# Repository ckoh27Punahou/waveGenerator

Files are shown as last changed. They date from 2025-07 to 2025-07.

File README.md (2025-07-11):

# Wave Generator Documentation

## Wave Generator Purpose

This project was developed to help support outreach efforts in Hawaii's educational sector, specifically in regards to further educating the use about waves and wave energy. 

This github page aims to provide adequate documentation for a desktop wave generator. It should provide **CAD Files, COTS BOM, Electrical Diagrams, and Source Code**. 

# CAD Files

## File Formatting

This wave generator is constructed using 3D printed and supplementary COTS parts (Commercial Off The Shelf). **The CAD files are posted as .STEP files**, meaning that they are ***NOT*** meshes (fully editable geometry). 

## Print Settings

The 3D printed parts (for working models) should be printed out of PLA or PETG. Settings are as follow: 3-5 walls, 25-45% infill. Prints should be within +-0.2mm of tolerance. Adjust to printer as necessary. 

## CAD BOM

The [Bill of Materials](https://github.com/ckoh27Punahou/waveGenerator/blob/main/Docs/waveGeneratorBOM.csv) to all of the COTS parts is posted as a .csv within the Docs folder. 

# Source Code

This wave generator uses code to take user input via rotary encoders and calculate the proper settings to generate the user specified waves. There are two options for source code: using Visual Studio's Platform IO, or using the official Arduino IDE. There are two versions of the code posted above (identical) - each is designed for the specific program. 

## Development Platforms

This code was developed specifically for the [Arduino Nano ESP32](https://store.arduino.cc/products/nano-esp32-with-headers?srsltid=AfmBOoobrec-nGruFs_-Y9yvGQ6Ko73yMo6Cp1iv4HudvSx1w5w5968Y) using the Arduino configuration. The development platform was Visual Studio Code, which utilized Platform IO to push the code to the Arduino and include the necessary libraries. Versions for the Arduino IDE and VS Code are both posted above (**Install Accordingly**). 

## Installing Libraries

The following library dependencies need to be installed (either using Platform IO or the Arduino IDE): AccelStepper.h, hd44780.h, hd44780_I2Cexp.h - this is done externally of the written software. 

[How to install libraries in Platform IO](https://community.platformio.org/t/adding-libraries-to-project/25807)

[How to install libaries in Arduino IDE](https://docs.arduino.cc/software/ide-v1/tutorials/installing-libraries/)

# Electrical Wiring

[Electrical wiring diagram](https://github.com/ckoh27Punahou/waveGenerator/blob/main/Docs/waveGeneratorElectricalDiagram.pdf) is posted in the Docs folder ("waveGeneratorElectricalDiagram.pdf"). 

# Assembly

Assembly for this project is relatively simple. It goes as follows: electrical assembly and wiring, installing heat-set inserts, physical assembly, belt tensioning, and finally mounting. 

[Full assembly instructions](https://github.com/ckoh27Punahou/waveGenerator/blob/main/Docs/AssemblyInstructions.md) is posted in the Docs folder ("AssemblyInstructions.md")

# Usage

Usage for this project is relatively straightforward. After code has been uploaded and mechanical and electrical systems have been constructed, the following instructions can be used: 

[Usage Instructions](https://github.com/ckoh27Punahou/waveGenerator/blob/main/Docs/UsageInstruction.md)

# Developer Notes

I'm Charlie Koh. At the time of this development, I am a rising Junior at Punahou High School. This project was developed in collaboration with the lab of Dr. Troy Heitmann.

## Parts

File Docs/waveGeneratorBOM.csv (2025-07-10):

Item # | Description | Link | Unit Quantity | Unit Price | Price
1 | Nema 17 | https://www.amazon.com/STEPPERONLINE-Stepper-Bipolar-Connector-compatible/dp/B00PNEQKC0 | 1 | $19.99 | $19.99 | Total Price
2 | DM556Y Stepper Driver | https://www.amazon.com/STEPPERONLINE-Digital-Stepper-1-7-5-6A-20-50VDC/dp/B082CWMTV2 | 1 | $25.19 | $25.19 | $134.51
3 | 20x4 LCD Display | https://www.amazon.com/Hosyond-Module-Display-Arduino-Raspberry/dp/B0C1G9GBRZ | 1 | $5.67 | $5.67
4 | Rotary Encoder | https://www.amazon.com/WGCD-KY-040-Degree-Encoder-Arduino/dp/B07B68H6R8 | 2 | $1.56 | $3.12
5 | 24v to 5v Buck Converter | https://www.digikey.com/en/products/detail/pololu/2858/10451183 | 1 | $18.95 | $18.95
6 | 300mmx8mm Carbon Fiber Rod | https://www.amazon.com/FANCYWING-400MMX-1-0MM-Carbon-Airplane/dp/B0BJ1HZYZQ?sp_csd=d2lkZ2V0TmFtZT1zcF9hdGY | 4 | $4.40 | $17.60
7 | Timing Belt System | https://www.amazon.com/KeeYees-Timing-Tensioner-Torsion-Printer/dp/B07JKT5BZQ/ref=sr_1_15?sr=8-15 | 1 | $14.99 | $14.99
8 | 15mmx15mmx8mm Linear Bearing | https://www.amazon.com/RJ4JP-01-08-Bearing-Printer-Replacement-Diameter/dp/B099665RSK | 4 | $1.46 | $5.84
9 | 17mmx6mmx6mm Ceramic Bearing | https://www.amazon.com/gp/product/B0B5XN4FFV/ref=ewc_pr_img_1?smid=A1THAZDOWP300U&th=1 | 1 | $1.64 | $1.64
10 | M4 Heat Set Insert | https://www.amazon.com/HANGLIFE-Heat-Set-Threaded-Printing-Components/dp/B0CS6XGMFD | 30 | $0.10 | $3.00
11 | 20mm M4 Bolt | https://www.amazon.com/BNUOK-180pcs-Stainless-Threads-Spanner/dp/B0DYNJPYV7?sp_csd=d2lkZ2V0TmFtZT1zcF9tdGY | 22 | $0.07 | $1.54
12 | 12mm M4 Bolt | https://www.amazon.com/Fullerkreg-Socket-Stainless-Machine-Quantity/dp/B07CJ7PTRS?sp_csd=d2lkZ2V0TmFtZT1zcF9hdGY | 16 | $0.11 | $1.76
13 | 25mm Steel Dowel | https://www.amazon.com/ZDingTech-Support-Shelves-Rod-304-Stainless/dp/B0F28QSRGD | 1 | $0.23 | $0.23
14 | 1 kg PETG | https://www.amazon.com/Polymaker-PB01001-PolyLite-hitzebest%C3%A4ndig-Zugfestigkeit/dp/B09DKRTSXW?s=industrial&sp_csd=d2lkZ2V0TmFtZT1zcF9hdGY | 1 | $15 | $15

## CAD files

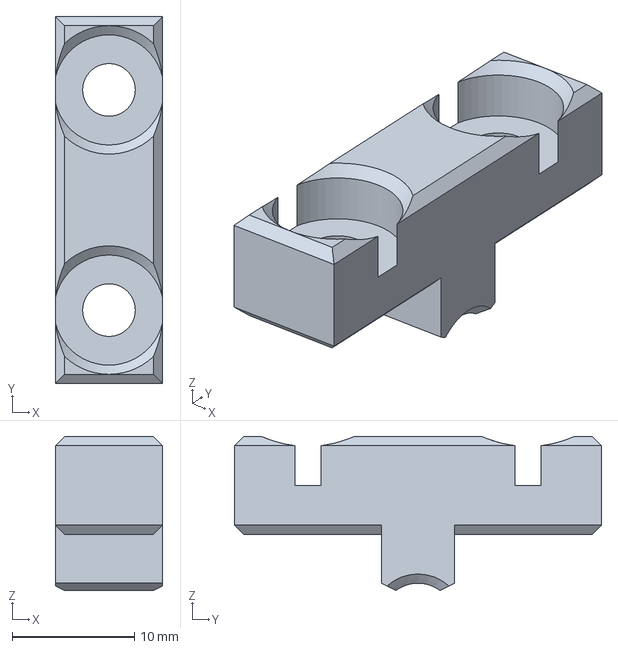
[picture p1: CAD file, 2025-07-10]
CAD_Files/Wave Generator CAD/Wave Generator - Pulley Seal 2.step
8.75 x 30.0 x 12.6 mm

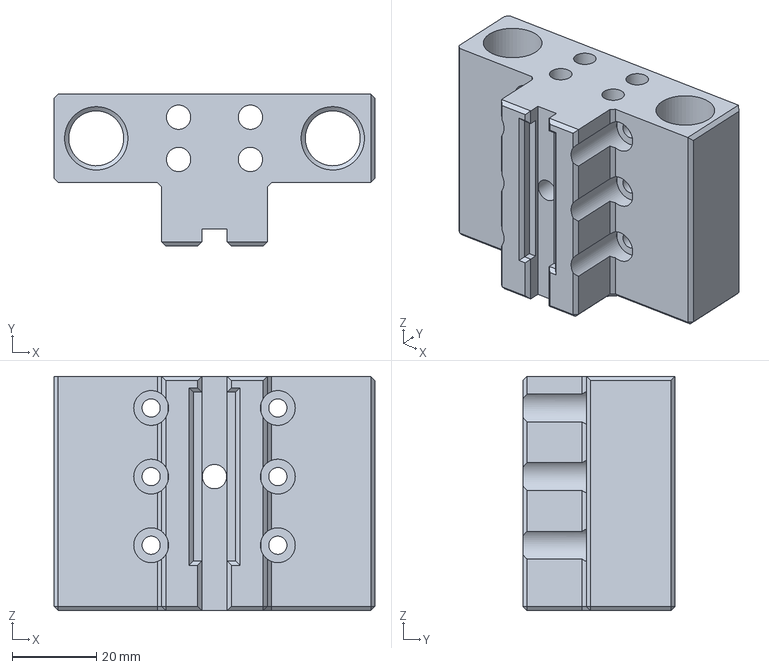
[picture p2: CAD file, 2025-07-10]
CAD_Files/Wave Generator CAD/Wave Generator - Wave Carrier.step
76.0 x 36.0 x 55.5 mm

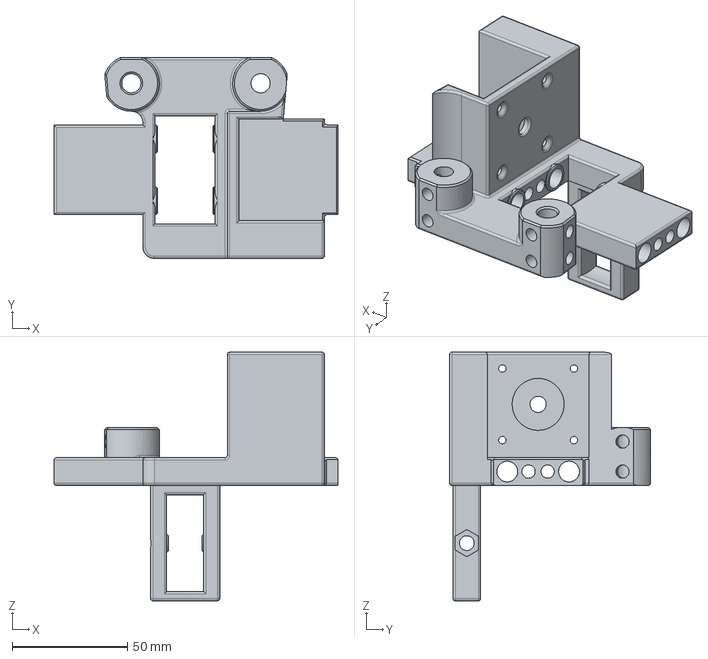
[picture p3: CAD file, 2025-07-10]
CAD_Files/Wave Generator CAD/Wave Generator - Motor Mount.step
123.0 x 87.0 x 107.7 mm

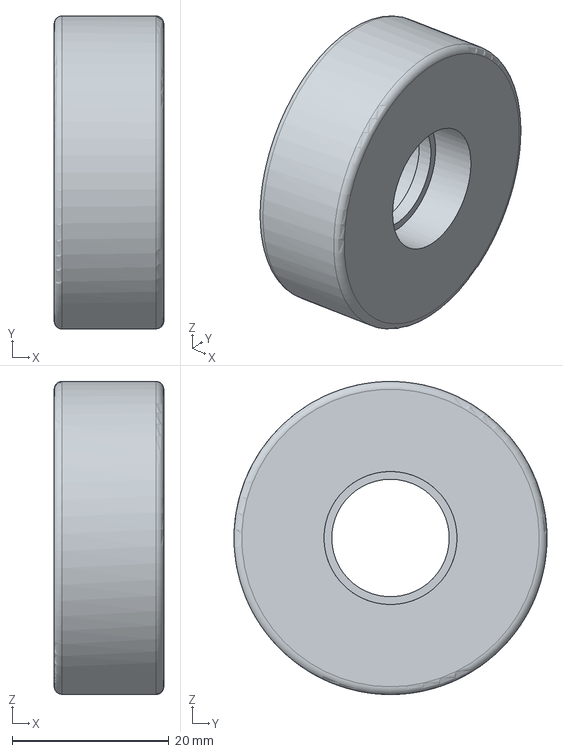
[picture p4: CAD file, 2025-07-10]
CAD_Files/Wave Generator CAD/Wave Generator - Idler Pulley.step
14.0 x 40.0 x 40.0 mm

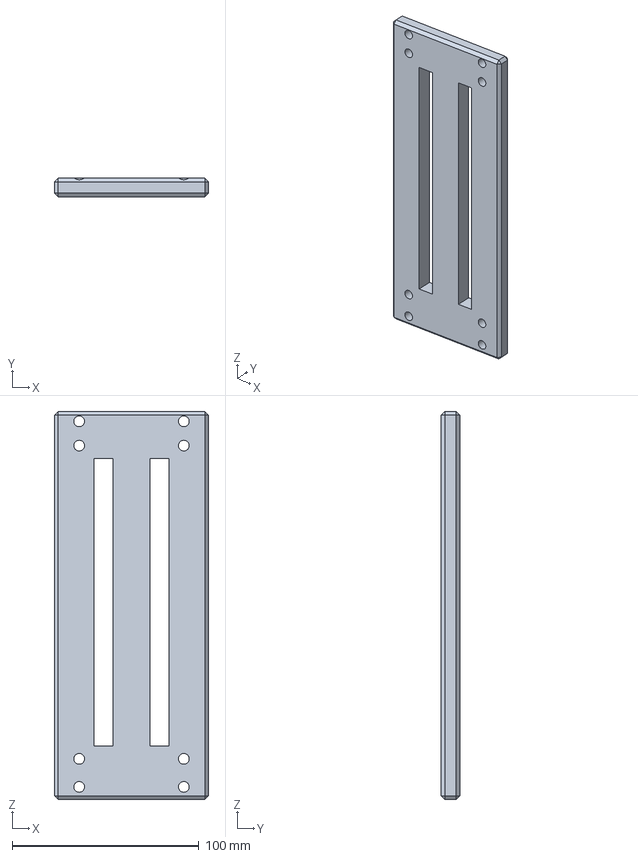
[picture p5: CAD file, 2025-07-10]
CAD_Files/Wave Generator CAD/Wave Generator - Wedge Backfill Cover.step
82.5 x 10.00 x 207.7 mm

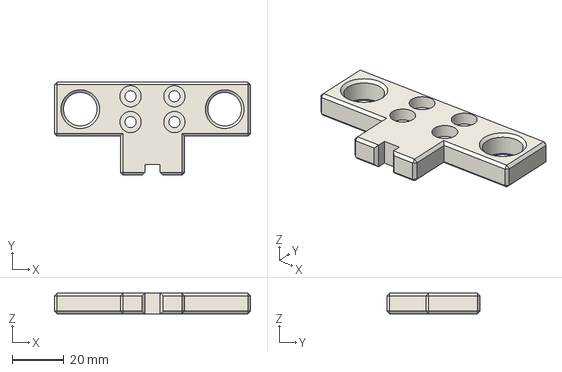
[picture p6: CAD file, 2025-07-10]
CAD_Files/Wave Generator CAD/Wave Generator - Wave Carrier Seal.step
76.0 x 36.0 x 8.00 mm

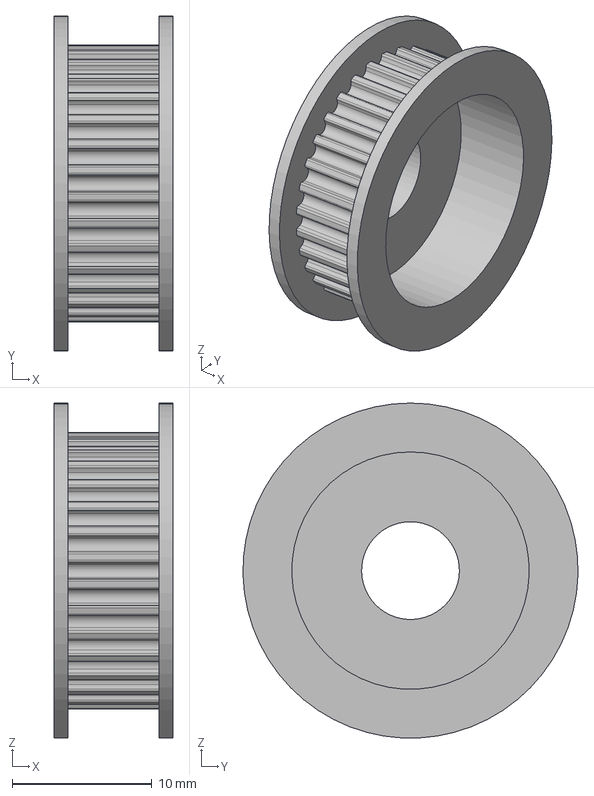
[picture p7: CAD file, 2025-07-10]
CAD_Files/Wave Generator CAD/Wave Generator - Lower Pulley.step
8.50 x 24.0 x 24.0 mm

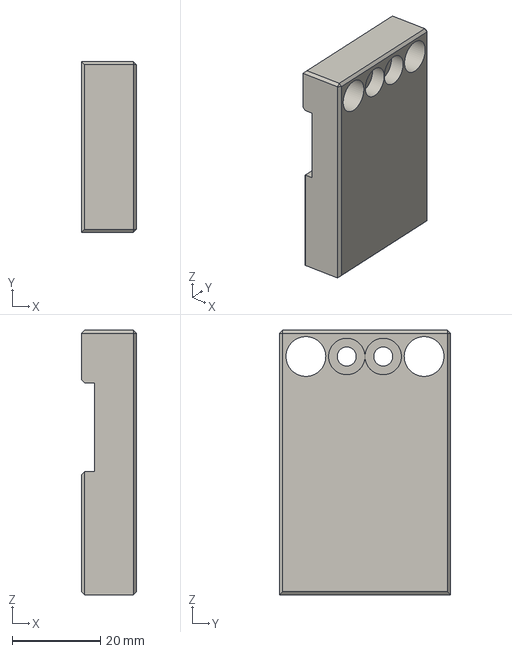
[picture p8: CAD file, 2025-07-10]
CAD_Files/Wave Generator CAD/Wave Generator - Outer Grab.step
12.5 x 38.8 x 60.0 mm

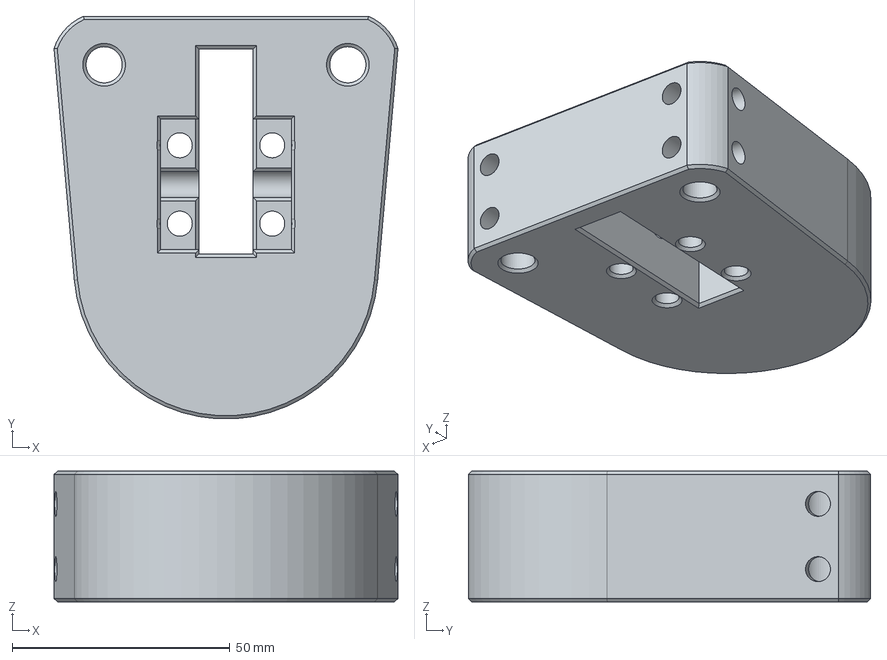
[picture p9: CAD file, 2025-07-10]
CAD_Files/Wave Generator CAD/Wave Generator - Lower Mount.step
79.0 x 92.5 x 30.0 mm

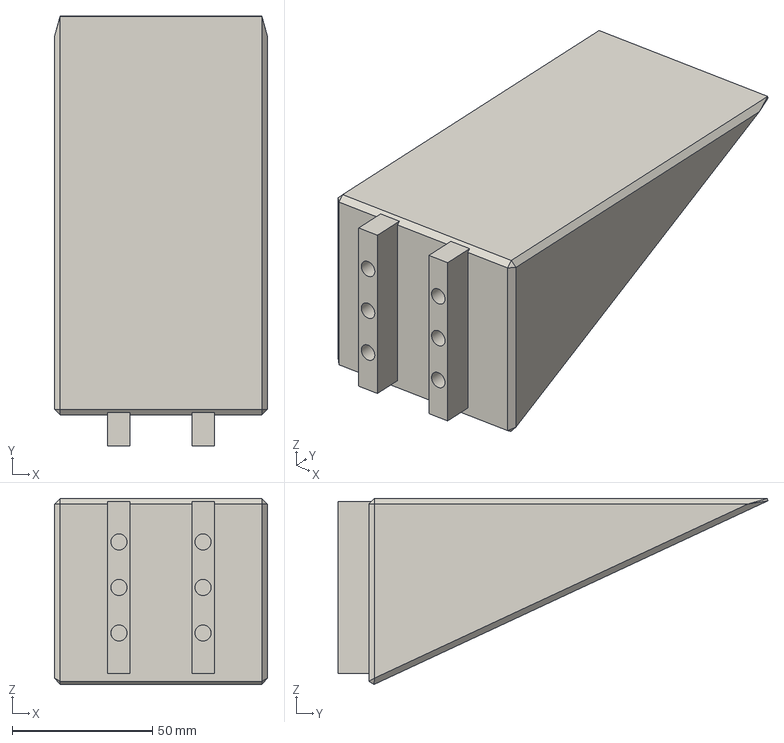
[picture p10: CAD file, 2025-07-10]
CAD_Files/Wave Generator CAD/Wave Generator - Wedge.step
76.0 x 153.4 x 66.4 mm

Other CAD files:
CAD_Files/Wave Generator CAD/Wave Generator - Pulley Seal.step
CAD_Files/Wave Generator CAD/Wave Generator - Outer Grab 2.step

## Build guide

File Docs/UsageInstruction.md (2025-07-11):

# Usage Procedure (Uploaded Arduino Code)

This is an instructional guide on how to use the wave generator after code has been uploaded. 

## Definitions (Repeated Later): 

**Wedge Angle:** The bottom angle of the wedge (between the hypotenuse and mounting side). Should be labeled at the top of the wedge. 
**Starting Depth:** The starting depth of the wedge. Measured as the deepest point of the wedge to the surface of the still water. Can be approximated (+-5mm). 
**Tank Depth:** The water depth in the tank. Measured from the bottom of the tank to the surface of the still water. 
**Amplitude:** The amplitude of the generated wave in millimeters. This is not completely accurate at the moment. During hardcaps (capping of amplitude at certain frequencies due to mechanical limits), the LCD will notify what the new hardcapped frequency is. The stroke length of the wedge corresponds with amplitude (via calculations involving all of the aforementioned variables and frequency), but does **not directly resemble the amplitude**. 
**Frequency:** The frequency of the generated wave in Hz. Frequency will always take priority over amplitude if mechanical limits are encountered (calculated by system internals - these are either speed caps or mechanical limits). 

## Step 0: Confirm Electrical Systems

Confirm that all electrical systems (particularly the buck converter) are wired exactly as the diagram shows. 

Move the wedge to the top of the movement range (as close as possible to the motor)

## Step 1: Plug Battery In

Plug the battery (24v 2.8aH) into the power adapter. The Arduino Nano ESP32 should have a small green LED light up. The motor driver (DM556Y) should also have a green LED light up. 

The LCD should light up, and should display some brief introduction text. 

## Step 2: Setting Initial Settings

### ***NOTE: You will not be able to change wedge angle, starting depth, or tank depth after the initialization phase. To reset, turn the system on and off***

After the LCD turns on, read the introductory text. After all text prompts disappear, it will ask to set a wedge angle. For this setting, either dial works to adjust the value (adjustments are +-1 degree). To confirm the value (after set to the desired value), push down on either of the dials (there is a button within the encoder).

It will then ask to set starting depth and tank depth. The top dial corresponds with starting depth, while the bottom dial corresponds with the tank depth. Set starting depth (the distance of the deepest wedge point from the surface of still water) and tank depth (the depth of water within the tank) to the nearest millimeter (adjustments are +-1 mm). To confirm starting depth, push down on the top dial. To confirm tank depth, push down on the bottom dial. 

After both starting and tank depth are confirmed, it will then ask for a **starting frequency and starting amplitude**. The top dial corresponds with amplitude, and the bottom dial corresponds with frequency. To confirm amplitude, press down on the top dial. To confirm frequency, press down on the bottom dial. 

***NOTE: Amplitude refers to the target amplitude of the WAVE, not the stroke. The stroke and rotation of the motor are calculated using all inputs.***

After a few brief seconds, it should start making waves. 

## Step 3 (Optional): Wave Amplitude and Frequency Adjustments

To adjust the wave amplitude and frequency without going through the entire setup, push down on either dial. It will pause wave generation as new settings are entered. The top dial again corresponds with amplitude, and the bottom dial is again with frequency. To confirm either, push down on the corresponding dial. 

A few seconds after both settings are confirmed, wave generation will resume, but with the adjusted settings.

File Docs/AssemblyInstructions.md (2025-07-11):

# Assembly Instructions

## Required Materials

1. Soldering Iron
2. Solder
3. BOM COTS Parts ($134.51)
4. 3mm Hex Key
5. Phillips Head Screwdriver
6. 2mm Hex Key
7. PLA
8. 20 AWG Wire
9. Dupont Jumper Cables
10. Wire Cutters
11. Wire Stripper
12. Heat Shrink/Electrical Tape

## Step 1: Electrical Wiring

Construct the electrical diagram as shown ("waveGeneratorElectricalDiagram"). The junctions indicate soldered areas/wire electrical connections. Wires that cross but do not contain a junction on their intersection do not have any electrical connection. For safety, place electrical tape/heat shrink over soldered joints. 

## Step 2: Heat Set Inserts

**NOTE: For this step, use a soldering iron tip either specifically designed for heat set inserts, or be comfortable having potential PLA contamintation on the tip of the soldering iron.**

Using M4 Heat Set Inserts (included in the COTS BOM), place heat set inserts in all of the following designated locations (images shown below). Arrows with label "1" indicate heat set inserts. 

Heat set inserts ***MUST*** be put in straight. If they are not, and screws insertion is attempted, the insert may do one of the following:

1. Surface detachment (pulled out)
2. Cross threading (destroys thread)
3. Unable to insert (either due to misalignment or angling)

### Upper Diagram:

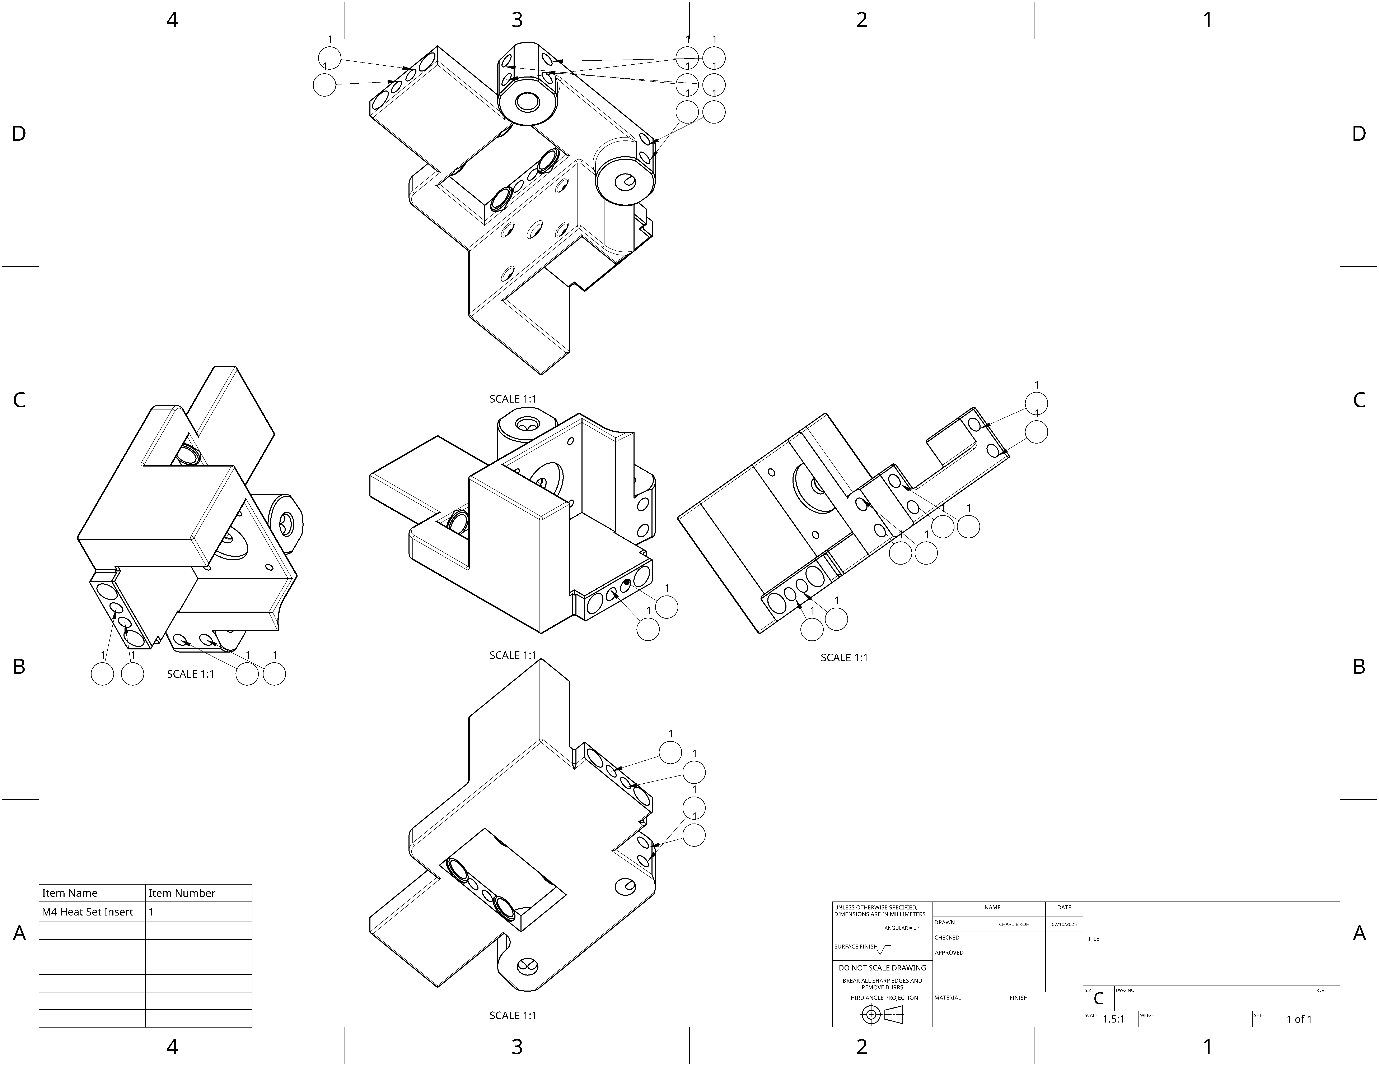
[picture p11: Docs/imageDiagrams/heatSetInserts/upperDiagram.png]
Upper Diagram


### Lower Diagram: 

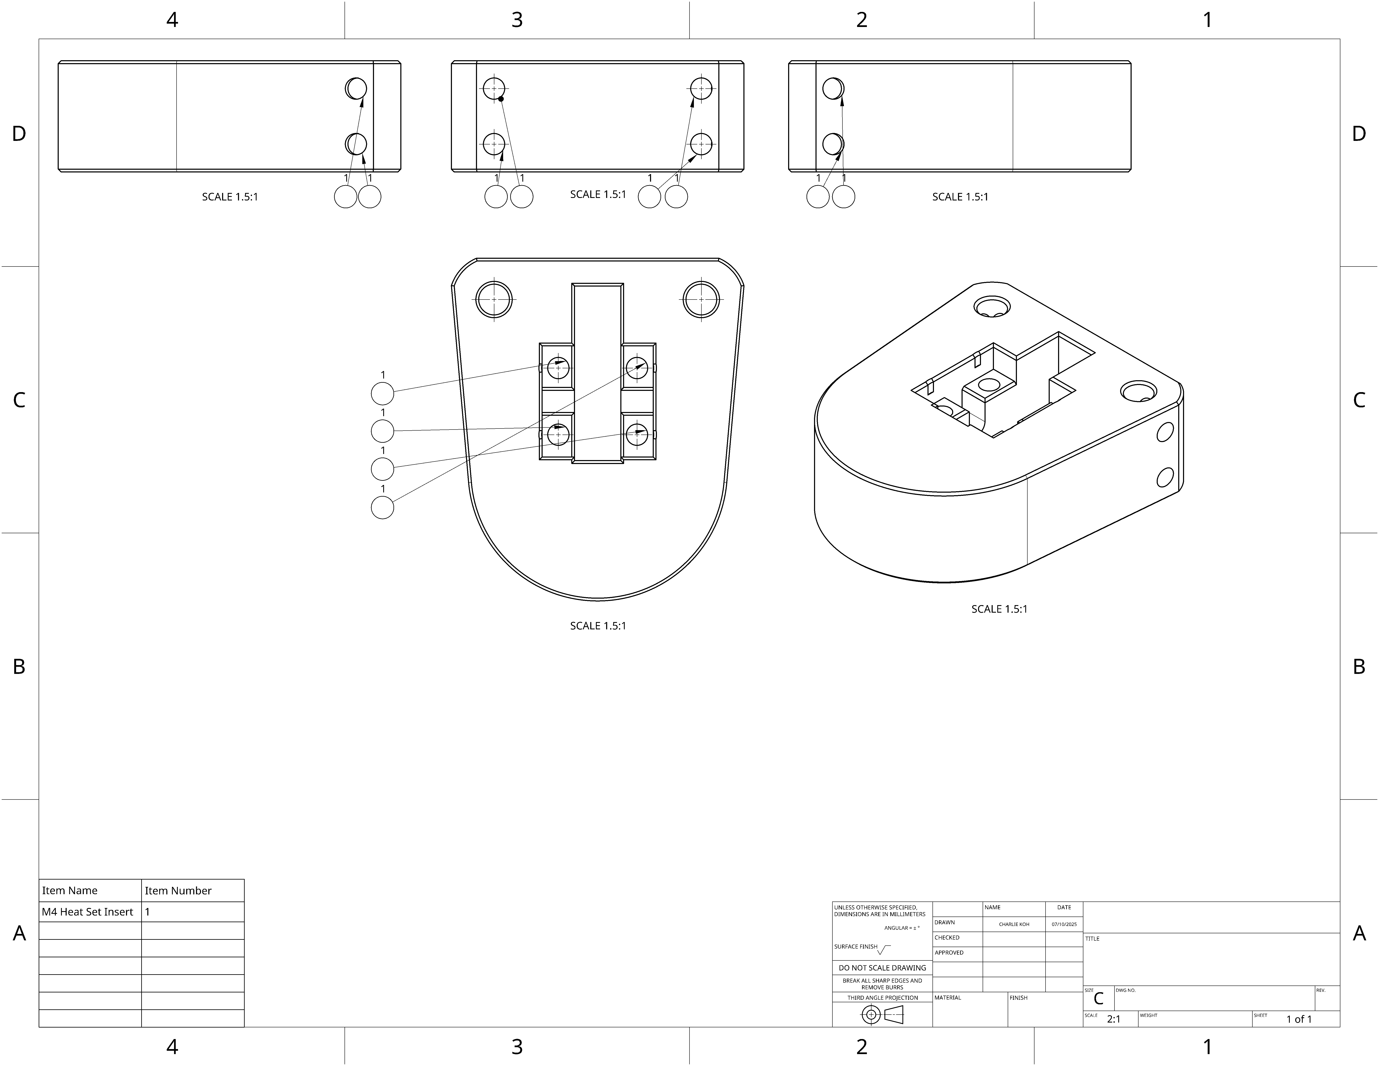
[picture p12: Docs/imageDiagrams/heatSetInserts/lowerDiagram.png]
Lower Diagram


### Wedge Diagram:

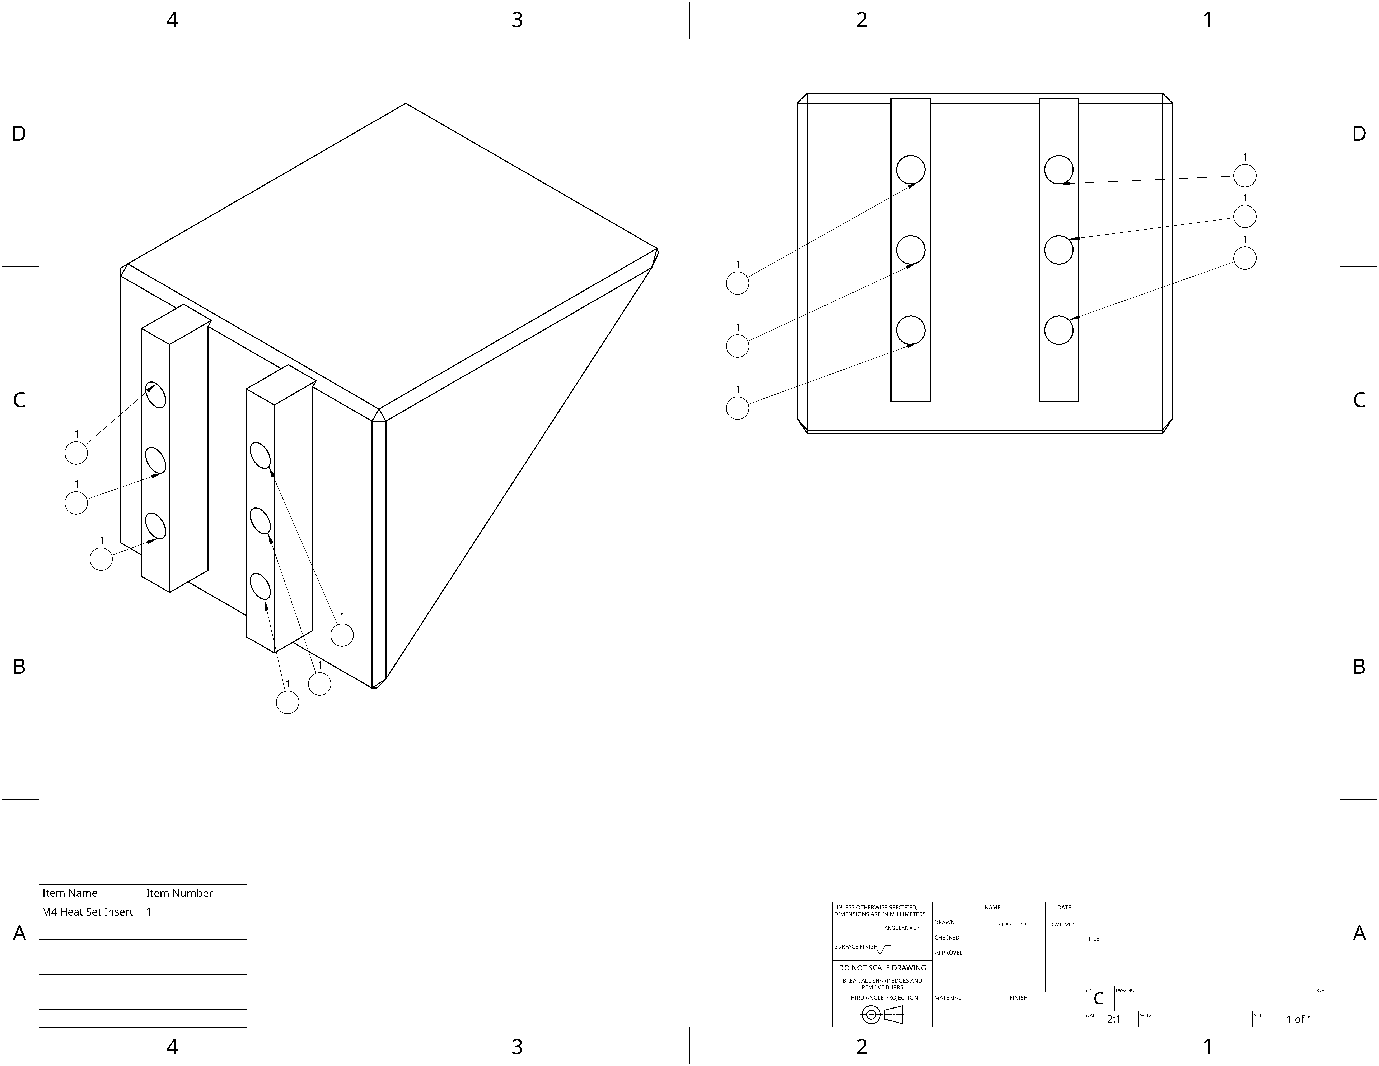
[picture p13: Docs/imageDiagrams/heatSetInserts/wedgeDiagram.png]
Wedge Diagram


## Step 3: Physical Assembly

### **Fully Exploded View**

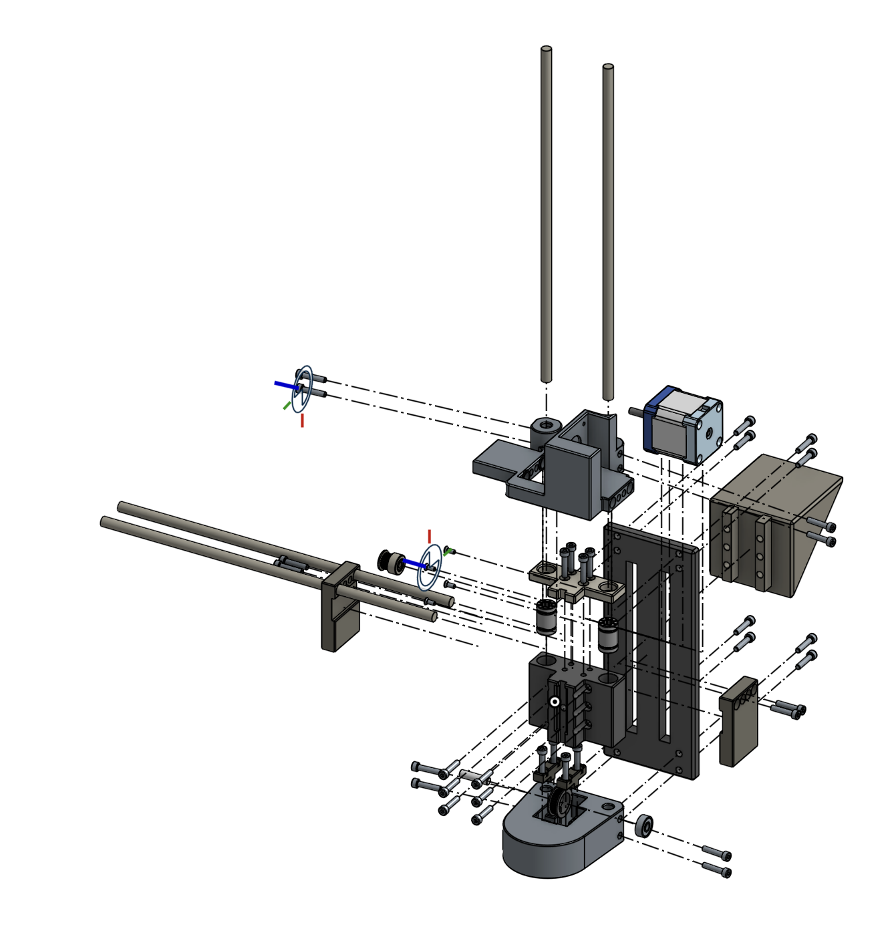
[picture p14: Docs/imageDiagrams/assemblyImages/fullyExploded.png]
Exploded View


### Step 3a: Insert Motor

Insert the motor as shown in the image below. Screw the motor in using the countersunk M3 screws (phillips head). 

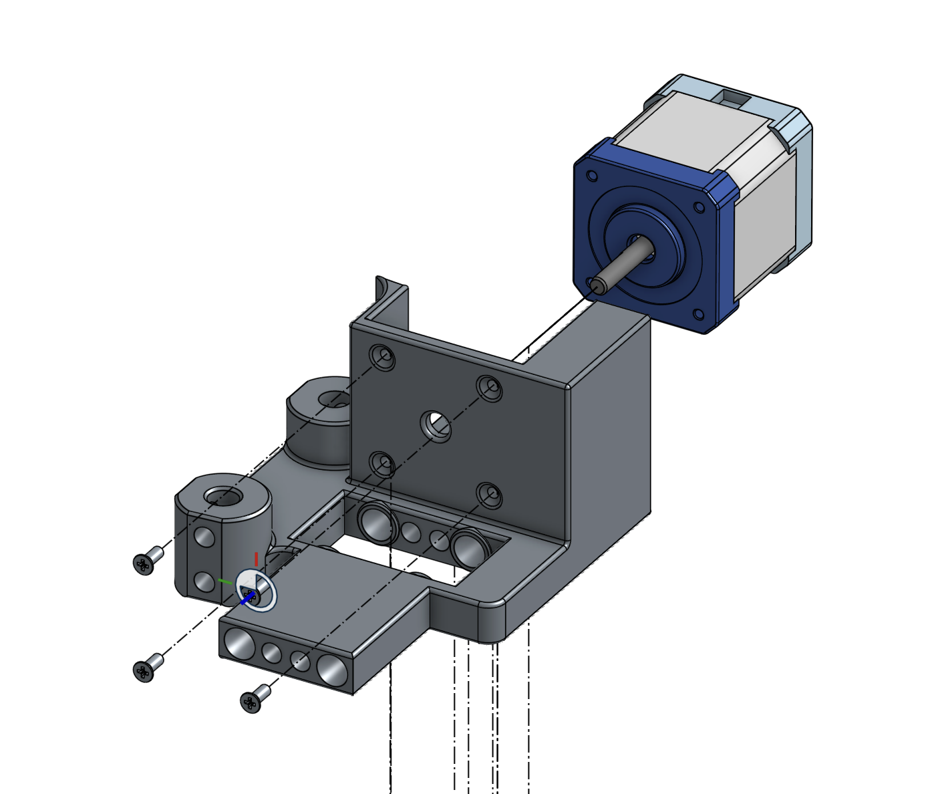
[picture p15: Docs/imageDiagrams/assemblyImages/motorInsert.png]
Motor Insert


### Step 3b: Insert Carbon Fiber Rod

Insert carbon fiber rod in the designated location of the motor mount. This won't be secured, and is used for structural support.

When inserting, make sure to simultaniously insert two linear bearings as shown below. These will be used to tension the belt.

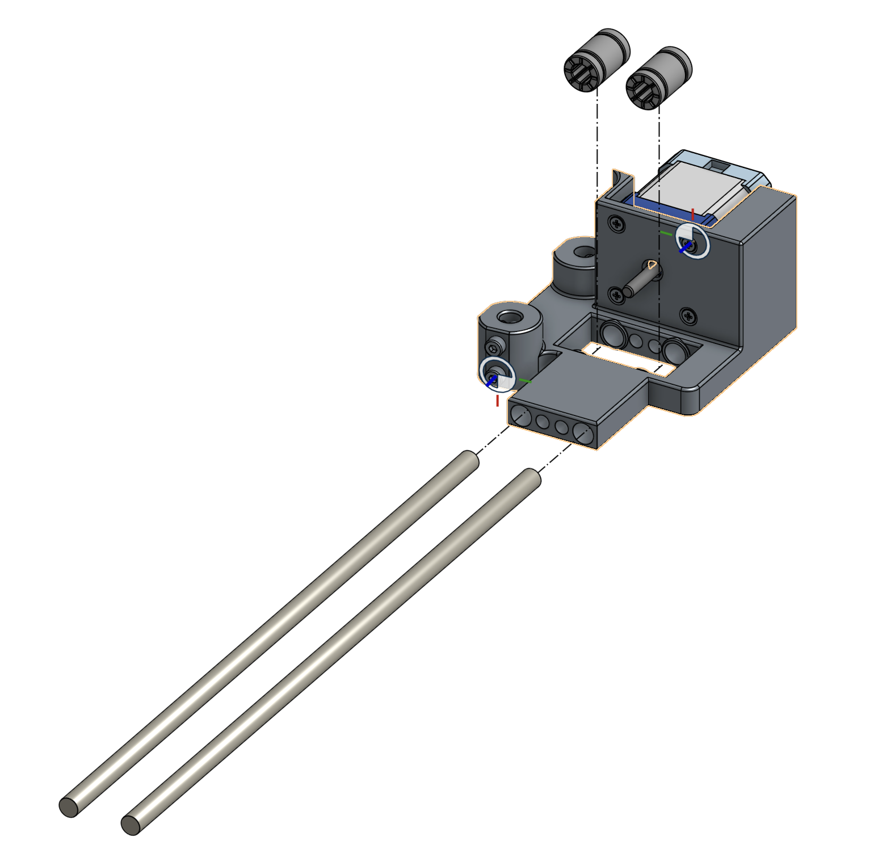
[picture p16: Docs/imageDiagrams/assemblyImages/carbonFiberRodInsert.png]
Carbon Fiber Rod Insert


### Step 3c: Assemble Carrier

Press fit linear bearings into the central carrige, and then screw the top cover onto the central carrige (as displayed below) using M4x20mm screws. 

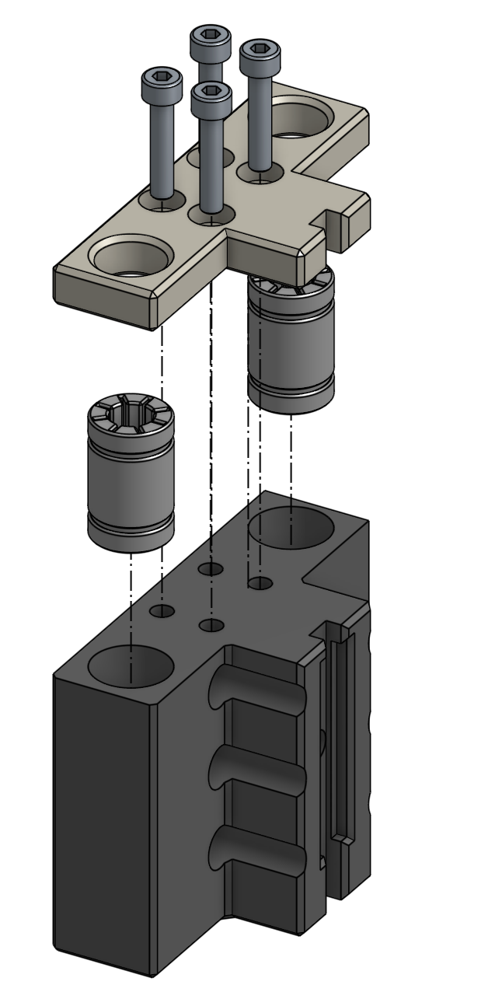
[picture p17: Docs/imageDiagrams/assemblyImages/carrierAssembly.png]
Carrier Assembly Diagram


### Step 3d: Assemble Lower Mount

Press fit 17mmx6mmx6mm bearing into lower pulley. Place pulley (with bearing) and pulley spacer onto 25mmx6mm steel dowel, and then insert into location on lower mount (displayed in image below).

Place lower seals to cover and secure 25mmx6mm steel dowel, and then secure with M4x20mm screws. 

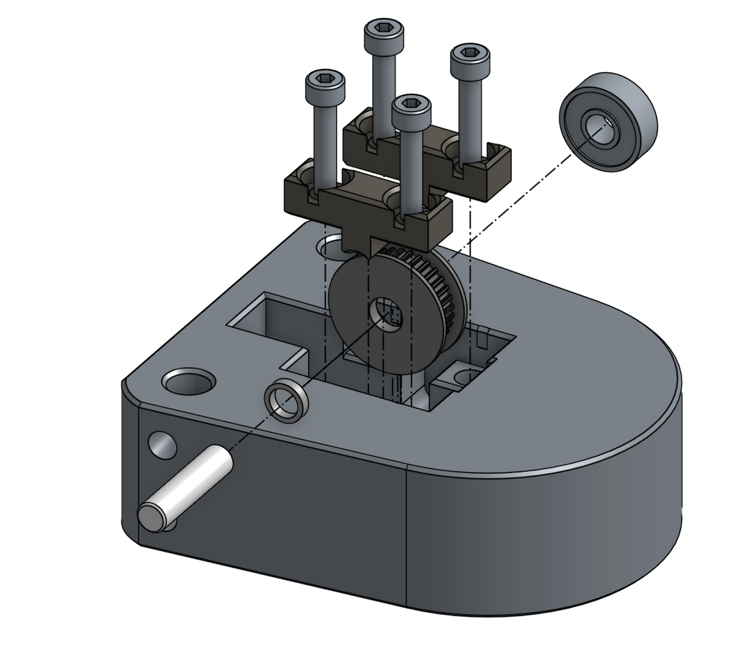
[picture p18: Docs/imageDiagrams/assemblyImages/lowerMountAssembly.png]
Lower Mount Assembly Diagram


### Step 3e: Insert Vertical Carbon Fiber Rods

Insert two 300mmx8mm Carbon Fiber Rods into the lower mount. Proceed to use M4x16mm screws to secure the carbon fiber rods (displayed in the image below - similar to set screws).

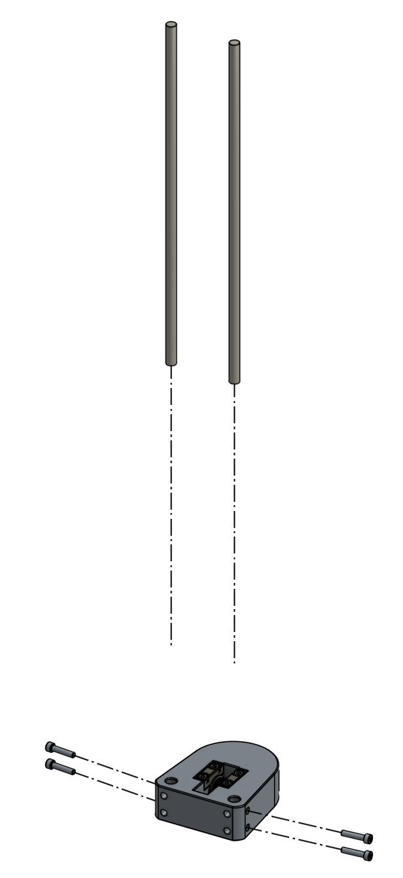
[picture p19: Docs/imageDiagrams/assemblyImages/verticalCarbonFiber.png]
Carbon Fiber Rod Insert


### Step 3f: Attach Motor Mount to Carbon Fiber Rods

Place the motor mount on the top of the two previously mounted vertical carbon fiber rods. Attach the front plate, and secure to the lower and motor mounts using M4x16mm screws. Similarly to the previous step, secure the carbon fiber rods with side M4x16mm screws (again, similar to set screws). 

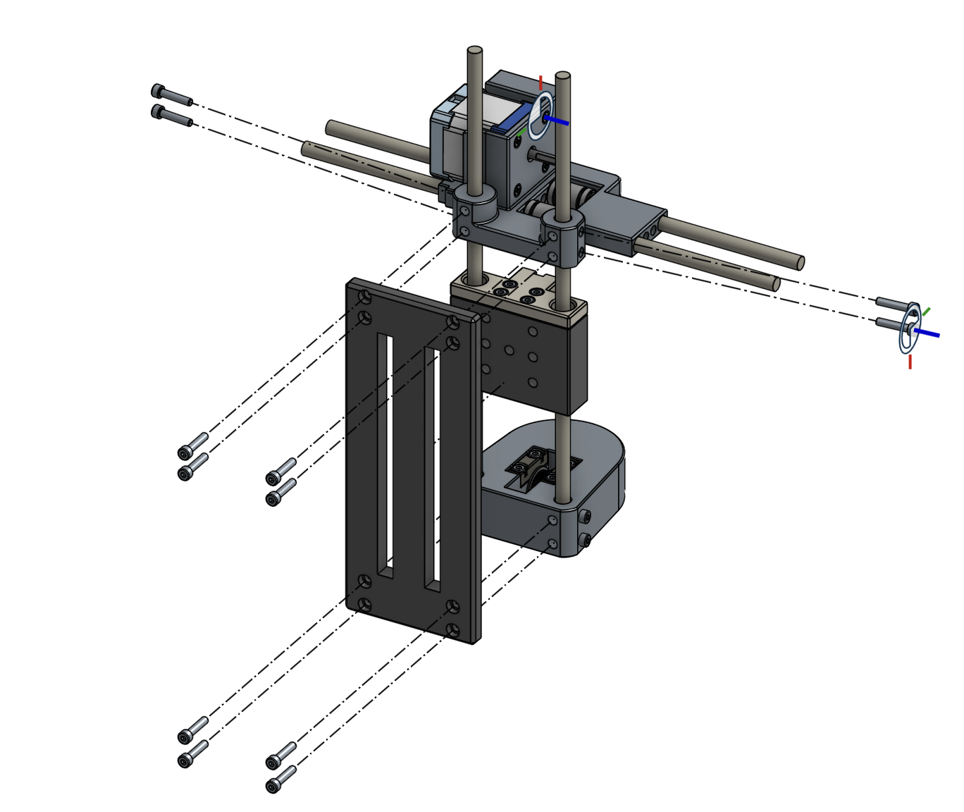
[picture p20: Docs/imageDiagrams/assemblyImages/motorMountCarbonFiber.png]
Motor Mount Carbon Fiber Insert


### Step 3g: Wedge Attachment

Place the front wedge stilts aligned with the central carrier. Use six M4x20mm screws to secure the wedge to the central carrier. 

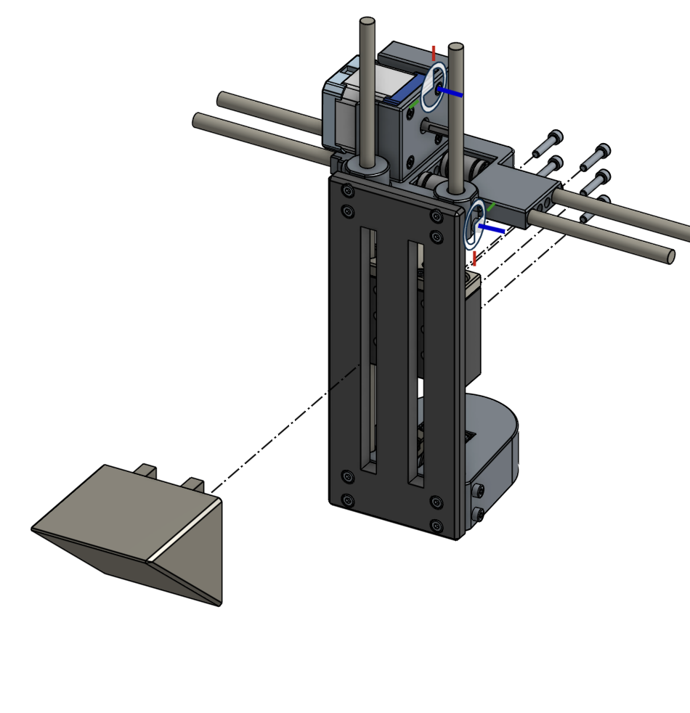
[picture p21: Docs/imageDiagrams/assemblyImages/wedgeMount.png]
Wedge Attachment Image


### Step 3h: Tank Mount 1

Place one of the outer mounts on the motor side of the motor mount, and secure it with two M4x20mm bolts. 

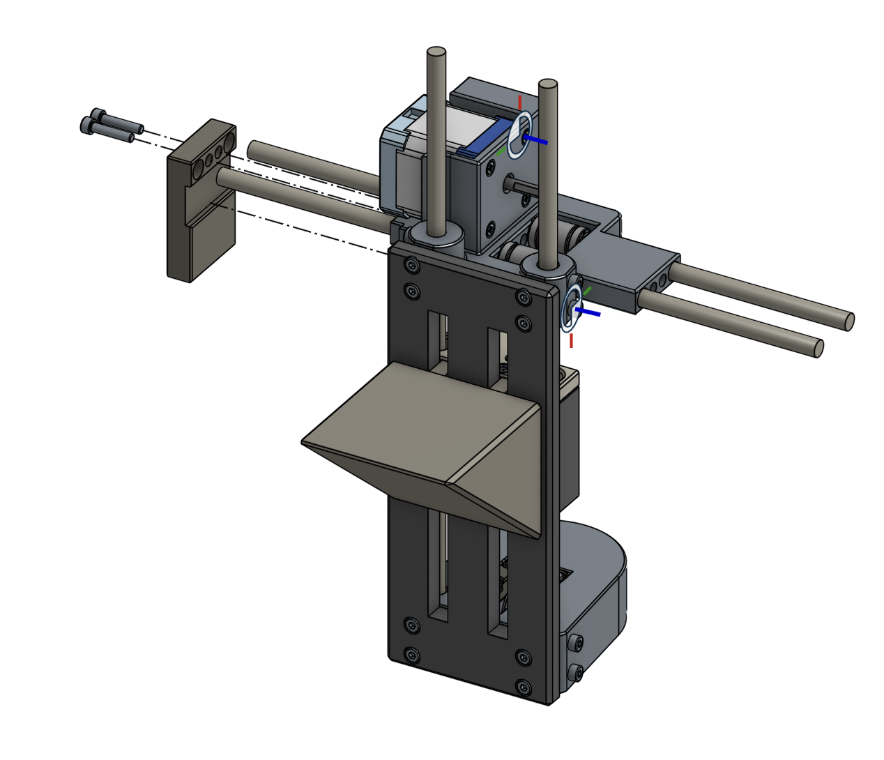
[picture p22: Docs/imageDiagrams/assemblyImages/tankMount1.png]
Tank Mount 1


### Step 3i: Mounting GT2 Pulley

Place 20T GT2 pulley onto the stepper motor shaft. 

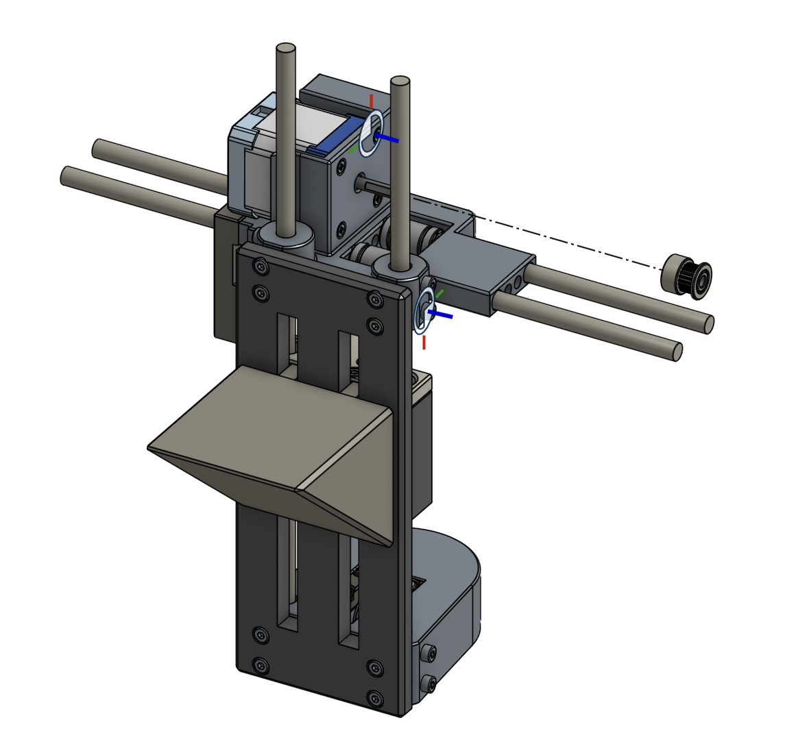
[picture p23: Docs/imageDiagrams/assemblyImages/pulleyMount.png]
Pulley Mounting


### Step 3j: Belt Mounting

Place belt around lower pulley and belt pulley, and place ends in the top and the bottom of the central carrier (not displayed). Place belt securer and M4x20mm bolt, and secure belt (with serrated side facing the belt and matching teeth) - make sure the belt is properly tensioned. 

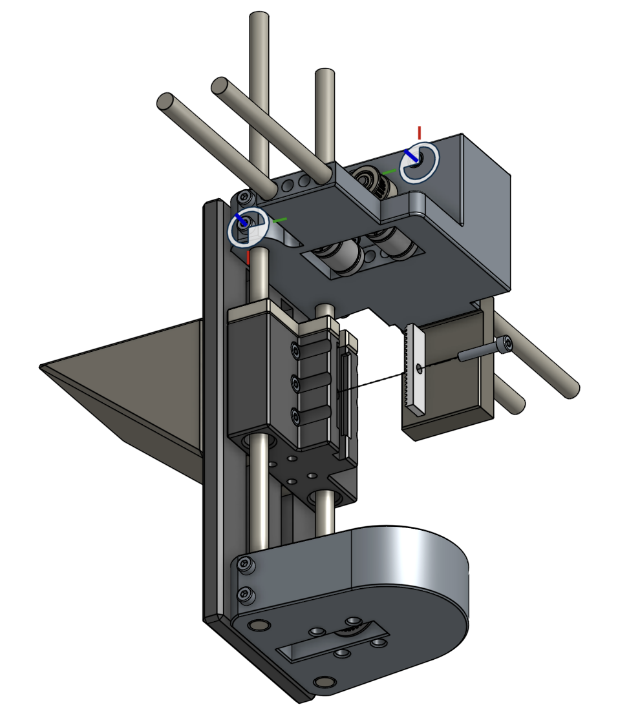
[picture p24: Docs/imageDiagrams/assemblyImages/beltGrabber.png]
Belt Mounting


### Step 3k: Tank Mounting

Place full assembly into the tank. Place second outer mount on the non-motor side of the motor mount, and secure around the tank using two M4x20mm screws.

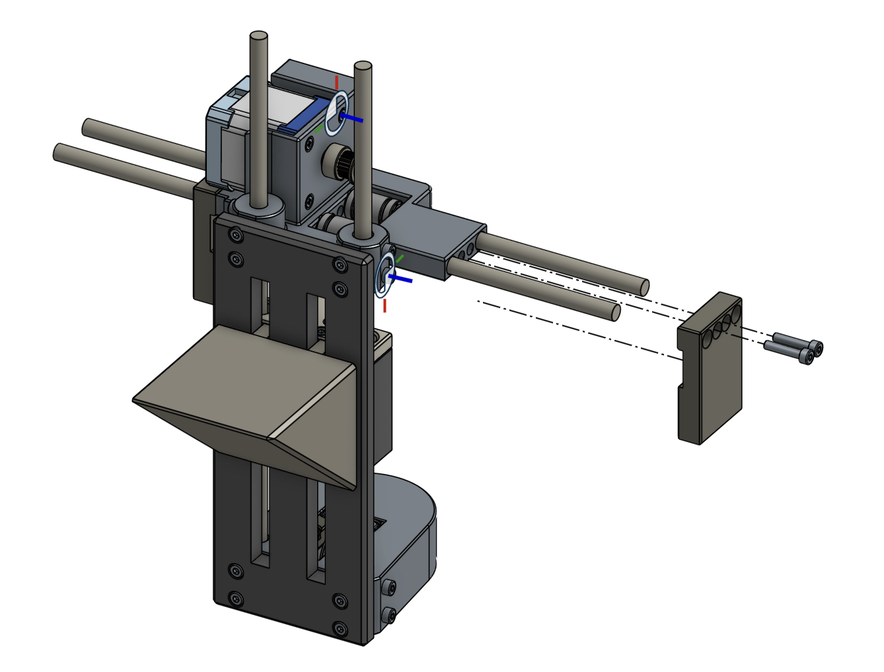
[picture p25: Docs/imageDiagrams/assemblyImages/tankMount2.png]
Tank Mounting


***Assembly of wave generator is completed***

## Step 4: Uploading Code

Prior to uploading code, choose to use either Visual Studio Code's Platform IO or the official Arduino IDE (easier). Download the corresponding file from this repository. 

Plug a data-capable USB-C cable into the Arduino Nano ESP32. Using either Platform IO or the Arduino IDE, make sure to import the following libraries (***NOT #include***): 

1. AccelStepper
2. hd44780
3. (For PIO, identify path) hd44780

[How to install libraries in Platform IO](https://community.platformio.org/t/adding-libraries-to-project/25807)

[How to install libaries in Arduino IDE](https://docs.arduino.cc/software/ide-v1/tutorials/installing-libraries/)

Using the computer port that the USB-C cable, upload the designed sketches (***Use the program either designed for Platform IO or Arduino IDE***). Once it states that uploding is complete, unplug the USB-C cable. 

***Transition to [User Manual](https://github.com/ckoh27Punahou/waveGenerator/blob/main/Docs/UsageInstruction.md) for usage instructions***

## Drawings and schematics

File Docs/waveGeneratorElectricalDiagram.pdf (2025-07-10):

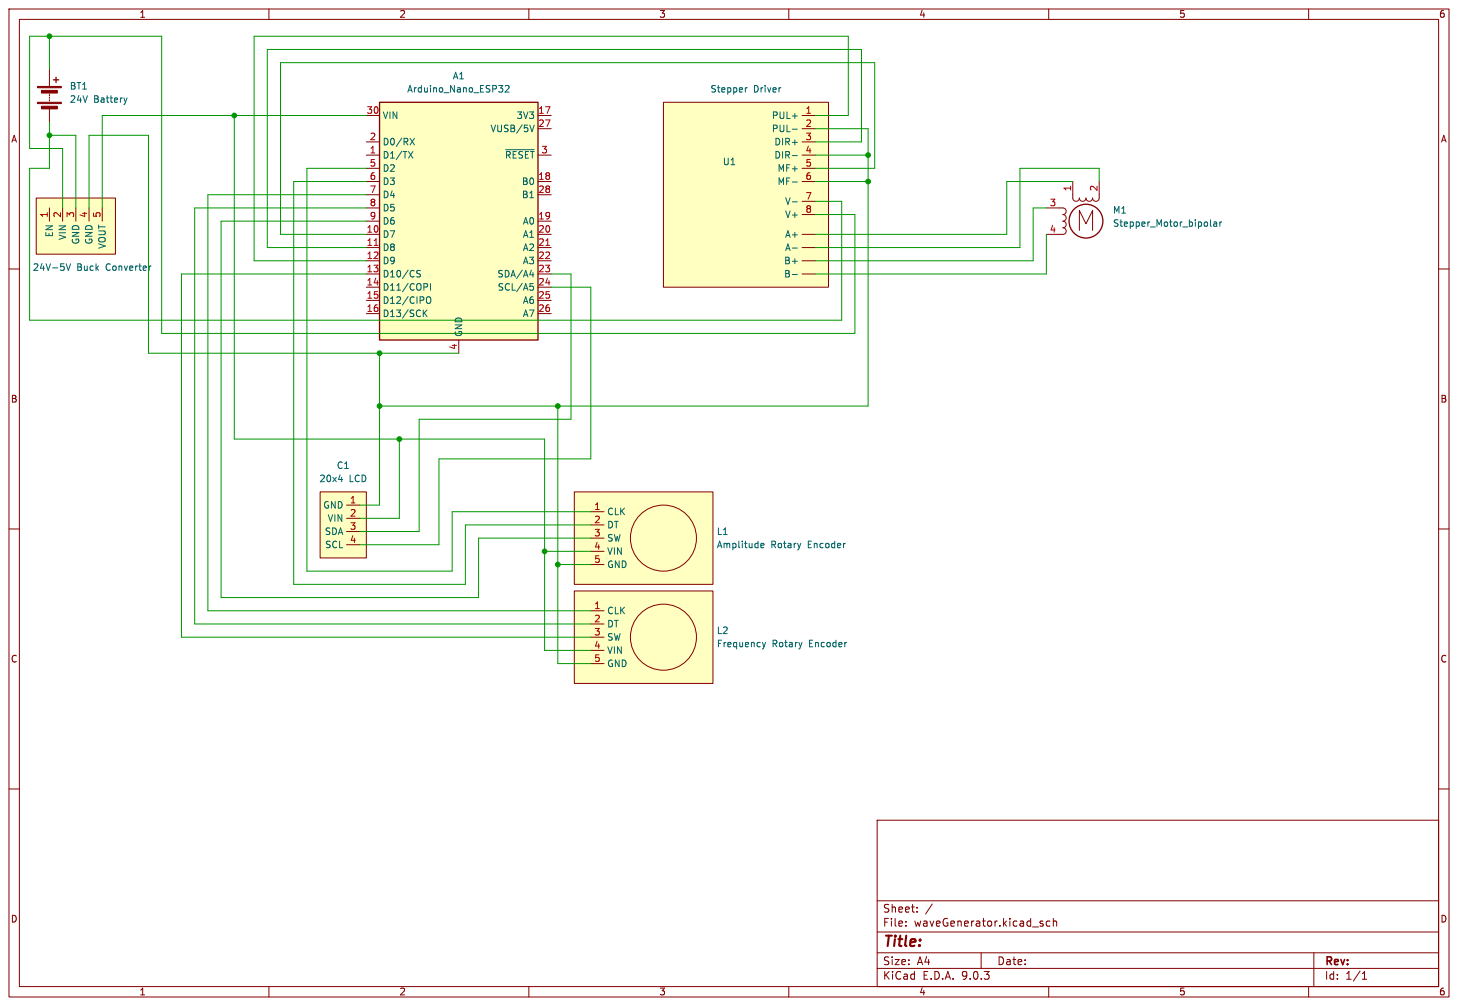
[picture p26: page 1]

2 M1 Stepper_Motor_bipolar CLK 1 DT 2 SW 3 VIN 4 GND 5

1 VIN
Id: 1/1 Title: File: waveGenerator.kicad_sch Sheet: / EN

L2Frequency Rotary Encoder CLK 1 DT 2 SW 3 VIN 4 GND 5

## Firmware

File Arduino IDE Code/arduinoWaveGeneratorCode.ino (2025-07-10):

// library imports 
// NOTE on Platform IO use: You will have to import all of the non-standard Arduino libraries using the Platform IO library interface

#include <Arduino.h> // imports the standard Arduino library - used in Platform IO (VS Code Arduino programming software)
#include <AccelStepper.h> // Mike McCaully's AccelStepperLibrary
#include <Wire.h> // one of the default Arduino libraries
#include <hd44780.h> // used to interface with LCD (by Bill Perry)
#include <hd44780ioClass/hd44780_I2Cexp.h> // IF NOT WRITTEN ON Platform IO (instead written in Arduino Studio), this path will be different!
#include <SPI.h> // one of the default arduino libraries

// Pin Variables

const uint8_t stepPin = 9; // step pin for the stepper motor driver (PUL+, STP+, etc.)
const uint8_t dirPin = 8; // direction pin for the stepper motor driver (DIR+)
const uint8_t enablePin = 7; // enable pin for the stepper motor driver (EN+, MF+, etc.)

const uint8_t ampClk = 2; // clk pin for the amplitude rotary encoder (detecting rotation + direction)
const uint8_t ampDt = 3; // dt pin for the amplitude rotary encoder (detecting rotation + direction)
const uint8_t ampSw = 6; // sw pin for the amplitude rotary encoder (button click)
const uint8_t freqClk = 4; // clk pin for the frequency rotary encoder (detecting rotation + direction)
const uint8_t freqDt = 5; // dt pin for the amplitude rotary encoder (detecting rotation + direction)
const uint8_t freqSw = 10; // sw pin for the frequency rotary encoder (button click)

// Various Constants

const int stepsPerRevolution = 200; // this will always be 200 (not to be confused with microsteps per revolution)
const int microsteps = 6400/200; // microsteps per step (total microsteps per rev/normal stepsPerRevolution)
const int maxSpeed = 80000; // max speed of motors in steps/sec
float acceleration = 2500*stepsPerRevolution*microsteps; // acceleration constant

const float stepInterval = 0.1; // not an interval for steps - adjusts the speed of adjustment for amplitude and frequency

float maxAmplitude = 10; // Maximum amplitude in mm
float minAmplitude = 0 - stepInterval; // Minimum amplitude in mm
float maxFrequency = 5; // Maximum frequency in Hz
float minFrequency = 0.1 - stepInterval; // Minimum frequency in Hz

const float pulleyPitch = 0.04; // the pitch diamter of the pulley in meters (40mm)
float maxStrokeLength = 35; // 1/2 of the available length of movement. This is technically 40mm, but it's set to give slight clearance

const float reduction = 0.8; // effective amplitude (experimental amplitude/theoretical amplitude) 
const float compensation = 1/reduction; // compensates for amplitude losses from experimental setups

const int loadingTime = 5000; // milliseconds between many of the display steps - allows for the users to read the instructions 

// Actual Variables

float tankDepth = 120; // the depth of water in the tank (in mm)
float startingDepth = 20; // the depth of the wedge beneath the surface (lowest point at start) - in mm
float wedgeAngle = 20; // the angle of the wedge submerged in the water (in degrees)

float amplitude = maxAmplitude; // adjustable amplitude
float frequency = maxFrequency; // adjustable frequency

bool ampConfirmed = false; // used to check user amplitude confirmation (can be seen later)
bool freqConfirmed = false; // used to check user frequency confirmation (can be seen later)

int ampCurrentClk; // current amp rotary encoder clk pin state (expressed as HIGH or LOW)
int freqCurrentClk; // current freq rotary encoder clk pin state (expressed as HIGH or LOW)
int ampPreviousClk; // previous cycle amp rotary encoder clk pin state (expressed as HIGH or LOW) - used for referencing changes
int freqPreviousClk; // previous cycle freq rotary encoder clk pin state (expressed as HIGH or LOW) - used for referencing changes

int ampSwitch; // checking the status of the amp rotary encoder button press (expressed as LOW when pressed, high when not)
int freqSwitch; // checking the status of the freq rotary encoder button press (expressed as LOW when pressed, high when not)

float targetPosition = 0; // target position stepper moves to (updated throughout running loop)
float targetSpeed; // target velocity of stepper motor (updated throughout running loop)
float maxRotation; // the amplitude of the motor movement pattern (the motor moves in a sin wave - this is the amplitude of wave)

String waveType = ""; // tells the wave type ("Deep", "Intermediate", or "Shallow") - depends on wave tank depth and wavelength

// Object Declarations

// Using the AccelStepper Arduino library

AccelStepper stepper(AccelStepper::DRIVER, stepPin, dirPin);

// Using the hd44780 & hd44780_I2Cexp Arduino libraries
// LCD is 20x4 connected via I2C port on Arduino (SDA and SCL - Pins A4 and A5 respectively)

hd44780_I2Cexp lcd;

// Calculating the wavelength of the wave given the frequency and tank depth

float waveLengthC(float frequency, float depth) {

  //Converting to period (reciprocal of frequency) 
  float T = 1 / frequency;

  // gravity constant
  float g = 9.81;

  // Iterative solving for wavelength - pulled from existing MatLab function 
  // https://www.mathworks.com/matlabcentral/fileexchange/48141-wavelength_calculator

  float L0 = (g*T*T)/(2*PI);
  float guess = L0;
  float L = (g*T*T)/(2*PI) * tanh((2*PI) * (depth/guess));
  float diff = abs(L-guess);

  // iterative guessing
  while (diff > 0.01) {
    diff = abs(L-guess);
    guess = L + (0.5 * diff);
    L = (g*T*T)/(2*PI) * tanh((2*PI) * (depth/guess));
  }

  // returns wavelength
  return L;
}

// calculate the stroke length from starting depth of wedge (startingDepth), amplitude of desired wave (amplitude), 
// wavelength of desired wave (calculated from frequency and tank depth) and wedge angle (theta)
// 

float stroke(float startingDepth, float amplitude, float wavelength, float theta) {
  // converting wedge angle to radians
  theta = theta * PI / 180.0;

  // converting amplitude from mm to meters
  amplitude = amplitude / 1000.0;

  // calculating length of stroke given input parameters
  // solving for equation 9 (https://www.sciencedirect.com/science/article/abs/pii/S0029801821013573)
  float strokeLength = -startingDepth + sqrt((amplitude*wavelength / (2*PI*tan(theta))) + (startingDepth*startingDepth));

  // adjust for 80% of wave height from numerical to experimental
  // compensation is reciprocal of % (80% of height -> 125% compensation)
  strokeLength = strokeLength * compensation;

  // return solved stroke length
  return strokeLength;
}

void setup() { // this section of code only runs once

  // Local waveLength declaration

  float waveLength = 0.0;

  // LCD Initialization 
  Wire.begin();
  lcd.begin(20,4);
  lcd.backlight();

  // Motor enable pulse
  pinMode(enablePin, OUTPUT);
  digitalWrite(enablePin, LOW);

  // Amplitude Rotary Encoder Initiation
  pinMode(ampClk, INPUT);
  pinMode(ampDt, INPUT);
  pinMode(ampSw, INPUT_PULLUP);

  // Frequency Rotary Encoder Initiation
  pinMode(freqClk, INPUT);
  pinMode(freqDt, INPUT);
  pinMode(freqSw, INPUT_PULLUP);

  // Setting initial state for rotary encoders
  ampPreviousClk = digitalRead(ampClk);
  freqPreviousClk = digitalRead(freqClk);

  // Initialization of motor settings
  stepper.setMaxSpeed(maxSpeed);
  stepper.setAcceleration(acceleration);
  stepper.setCurrentPosition(0);

  // stepper.moveTo(-200*microsteps);
  // while (stepper.distanceToGo() != 0) {
  //   stepper.run(); 
  // }

  //Introduction

  // Print on LCD
  lcd.clear();
  lcd.setCursor(0, 0);
  lcd.print("Wave Generator");
  lcd.setCursor(0, 1);
  lcd.print("Controls v1.1");
  lcd.setCursor(0, 3);
  lcd.print("Charlie Koh 2025");

  delay(loadingTime);

  lcd.clear();
  lcd.setCursor(0, 0);
  lcd.print("All units in mm");
  lcd.setCursor(0, 1);
  lcd.print("and Hz.");
  lcd.setCursor(0, 2);
  lcd.print("Click dial to");
  lcd.setCursor(0, 3);
  lcd.print("confirm values.");

  delay(loadingTime);

  lcd.clear();
  lcd.setCursor(0, 0);
  lcd.print("Max Frequency : ");
  lcd.setCursor(0, 1);
  lcd.print(maxFrequency + stepInterval);
  lcd.setCursor(0, 2);
  lcd.print("Max Amplitude: ");
  lcd.setCursor(0, 3);
  lcd.print(maxAmplitude + stepInterval);
  
  delay(loadingTime); 

  // Wedge Angle Confirmation - units are degrees
  bool wedgeAngleConfirmed = false;

  //User introduction
  lcd.clear();
  lcd.setCursor(0, 0);
  lcd.print("Set Wedge Angle.");
  lcd.setCursor(0,1);
  lcd.print("Units are Degrees. ");

  delay(loadingTime);
  lcd.clear();
  lcd.setCursor(0, 0);
  lcd.print("Wedge Angle (Deg): ");
  lcd.setCursor(0, 1);
  lcd.print(wedgeAngle);

  // While the switch on either potentiometer is not pressed 
  while (!wedgeAngleConfirmed) {
    //Updating readings on the different rotary encoders
    ampCurrentClk = digitalRead(ampClk);
    freqCurrentClk = digitalRead(freqClk);

    ampSwitch = digitalRead(ampSw);
    freqSwitch = digitalRead(freqSw);

    // detecting and registering change in either rotary encoder
    if (ampCurrentClk != ampPreviousClk || freqCurrentClk != freqPreviousClk) {
      // detects positive or negative movmement
      if (ampCurrentClk != digitalRead(ampDt) || freqCurrentClk != digitalRead(freqDt)) {
        wedgeAngle += 1;
      } else {
        wedgeAngle -= 1;
      }

      if (wedgeAngle < 0) { // ensuring does not dip below minimum value
        wedgeAngle = 0;
      }

      // Updating display values
      lcd.setCursor(0, 0);
      lcd.print("Wedge Angle (Deg.): ");
      lcd.setCursor(0, 1);
      lcd.print(wedgeAngle);
    }

    // Detecting encoder switch press (pressed returns a low value) on either switch
    if (ampSwitch == LOW || freqSwitch == LOW) {
      wedgeAngleConfirmed = true; // confirms button press (breaks the while loop conditional)
      lcd.setCursor(0, 0);
      lcd.print("Wedge Angle set!"); // tells user that it's been pressed
      delay(1000);
    }

    // updating rotary encoder values - rotary encoder compares previous values to current values to detect change
    // direction change is detected using digitalRead(dtPin) and comparing with Clk pin
    ampPreviousClk = ampCurrentClk;
    freqPreviousClk = freqCurrentClk;
  }

  // Setting starting depth and tank depth (units are mm for this measurement)
  lcd.clear();
  lcd.setCursor(0, 0);
  lcd.print("Set starting depth");
  lcd.setCursor(0, 1);
  lcd.print("and tank depth");
  lcd.setCursor(0, 2);
  lcd.print("Units are mm.");
  delay(loadingTime);

  // Conditionals defined for the while loop
  bool startingDepthConfirmed = false; // Amp Rotary Encoder corresponds
  bool tankDepthConfirmed = false; // Freq Rotary Encoder corresponds 

  // User display
  lcd.clear();
  lcd.setCursor(0, 0);
  lcd.print("Starting Depth (mm): ");
  lcd.setCursor(0, 1);
  lcd.print(startingDepth);
  lcd.setCursor(0, 2);
  lcd.print("Tank Depth (mm): ");
  lcd.setCursor(0, 3);
  lcd.print(tankDepth);

  while (!startingDepthConfirmed || !tankDepthConfirmed) { // while either or both are not confirmed (button not pressed)
    
    // updating rotary encoder values
    ampSwitch = digitalRead(ampSw); 
    freqSwitch = digitalRead(freqSw);

    ampCurrentClk = digitalRead(ampClk);
    freqCurrentClk = digitalRead(freqClk);

    if (ampCurrentClk != ampPreviousClk && !startingDepthConfirmed) { // If not confirmed, and change in corresponding encoder value
      // amp = starting depth
      // detecting positive or negative changes
      if (ampCurrentClk != digitalRead(ampDt)) {
        startingDepth += 1;
      } else {
        startingDepth -= 1;
      }

      if (startingDepth < 0) { // ensuring does not dip below minimum value (minimum is minimum value, in this case 0)
        startingDepth = 0;
      }

      // user interface
      lcd.setCursor(0, 0);
      lcd.print("Starting Depth (mm): ");
      lcd.setCursor(0, 1);
      lcd.print(startingDepth);
    }
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

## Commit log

2025-07-10 Pushing CAD Files
    [Wave Generator - Idler Pulley.step, Wave Generator - Lower Mount.step, Wave Generator - Lower Pulley.step, Wave Generator - Motor Mount.step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]
2025-07-10 Assembly Instructions
2025-07-10 Doc update and BOM Push
    [Wave Generator BOM Final - Wave Generator BOM.csv]
2025-07-10 Image Insert
2025-07-10 Diagram insertion into instructions.
2025-07-10 Updating assembly instructions
    Testing image insertions and formatting.
2025-07-10 Finalized wave assembly manual push
2025-07-10 Updated assembly instructions and creation of usage instructions.
2025-07-10 Structural Updates
    [Wave Generator - Idler Pulley.step, Wave Generator - Lower Mount.step, Wave Generator - Lower Pulley.step, Wave Generator - Motor Mount.step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]
2025-07-10 Adding the code.
    [waveGeneratorBOM.csv]
